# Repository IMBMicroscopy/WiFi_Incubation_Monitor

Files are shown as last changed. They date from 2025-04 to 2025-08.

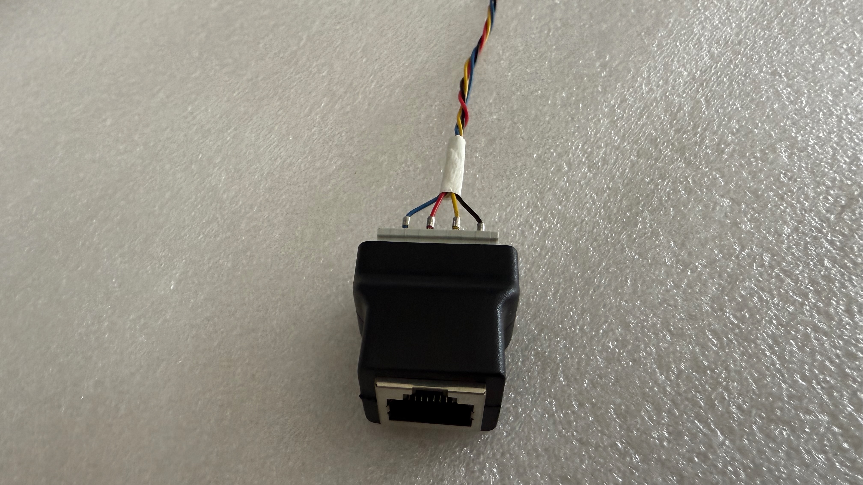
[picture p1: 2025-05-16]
Assembly Images/Front Side RJ45.jpeg

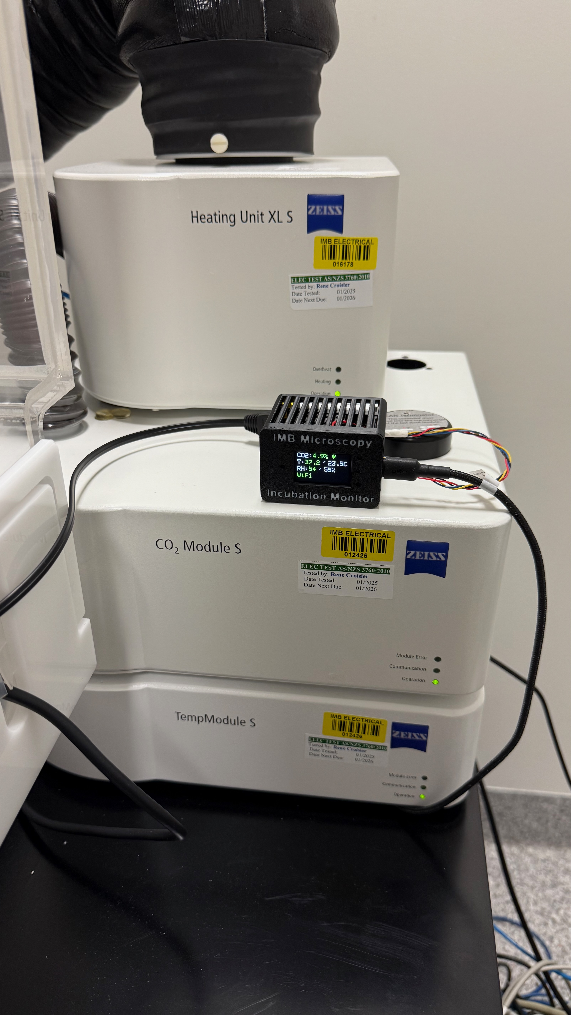
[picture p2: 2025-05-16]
Assembly Images/Monitoring CO2.jpeg

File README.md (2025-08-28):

# WiFi enabled Incubation Monitor

Author: Dr James Springfield (j.springfield@imb.uq.edu.au). 

Affiliation: Institute for Molecular Bioscience (IMB) Microscopy Facility, The University of Queensland. 

Date: June 2025. 

Real-Time Imaging Environment Monitoring Using an ESP32

We present a low-cost, open-source ESP32-based system for monitoring environmental conditions within live-cell imaging incubators. Each device integrates a 0–100% CO₂ sensor (with optional high-accuracy 0–1% sensor), along with temperature and humidity sensors. Optional features include pressure calibration and room environment monitoring.

A built-in TFT display and Adafruit IO dashboard provide real-time and remote data access. Sensor calibration compensates for temperature, humidity, and pressure. The system is user-friendly, requiring no soldering and offering hotspot-based configuration. It supports automated logging, WiFi setup, and dashboard customisation for scalable deployment across multiple incubators.

We are currently developing additional features, including Google Sheets integration for data logging, aligning with existing systems that track hardware and software usage during user sessions. These metrics are imported into Microsoft Power BI to generate dashboards that inform user needs and forecast future facility requirements.

updated incubation monitor





Pecon incubator lid inverted

Pecon lid installed

Monitoring CO2

## Monitor environmental conditions for live samples using an ESP32 device with STC31 CO2 sensor and SHTC3 temperature and relative humidity sensors

- Calibrate the CO2 sensor using Temperature, Humidity and Pressure
- Monitor LiPo battery SOC and discharge rate
- Report values to the TFT display, serial port and online dashboard
- **Each device will record the conditions for ONE incubator**
- **A free Adafruit IO account is required for logging of incubation conditions over time to the online dashboard**
  - https://accounts.adafruit.com/users/sign_in
  - You will then need the Username and Active Key values to load into the ESP32 device to enable data streaming.
  - **This must be done before configuring the hardware below**

**Required hardware:**

- Arduino compatible hardware such as: the following tested hardware
- Adafruit Feather ESP32-S3 reverse TFT mainboard such as https://learn.adafruit.com/esp32-s3-reverse-tft-feather (the code for the TFT has been optimised for this display size/resolution and will require modification for other displays)
- STC31 CO2 sensor board such as [https://www.sparkfun.com/products/18385](https://www.sparkfun.com/products/18385) or https://sensirion.com/products/catalog/SEK-STC31-C 
- Sparkfun Qwiic connector 500mm (or longer) cable: [https://www.sparkfun.com/products/17257](https://www.sparkfun.com/products/17257) (or you may manually solder the cables)
- This minimum configuration requires no soldering or electronics knowledge

**Required software libraries:**

- "SPI.h" built in library for SPI comms to tft display

- "WiFi.h" library for inbuit wifi comms to online dashboard

- "Preferences.h" for saving parameters to Flash for reuse later

- "SparkFun_STC3x_Arduino_Library.h" CO2 sensor library [http://librarymanager/All#SparkFun_STC3x](http://librarymanager/All#SparkFun_STC3x)

- "SparkFun_SHTC3.h" Temperature and Relative Humidity sensor library [http://librarymanager/All#SparkFun_SHTC3](http://librarymanager/All#SparkFun_SHTC3)

- "Adafruit_SHT4x.h" //SHT4x Temp/RH sensor library for use with the SEK-STC31-C development kit http://librarymanager/All#Adafruit SHT4x

- "Adafruit_GFX.h" Core graphics library for TFT display [http://librarymanager/All#Adafruit_GFX_Library](http://librarymanager/All#Adafruit_GFX_Library)

- "Adafruit_ST7789.h" Hardware-specific library for ST7789 controller [http://librarymanager/All#Adafruit_ST7789](http://librarymanager/All#Adafruit_ST7789)

- Adafruit IO Arduino Library [http://librarymanager/All#Adafruit_IO_Arduino](http://librarymanager/All#Adafruit_IO_Arduino)

  - "AdafruitIO_WiFi.h" for data feed functionality
  - "WiFiManager.h" for configuration of the sensors and WiFi

**Optional:**

- 3D printed case: AutoDesk Fusion https://a360.co/4j8FKbL or see included .3mf file
- Atmospheric pressure BME280 sensor [https://www.sparkfun.com/products/15440](https://www.sparkfun.com/products/15440) to measure atmospheric pressure for CO2 sensor calibration (also used for room T and RH monitoring)
- Adafruit BME280 Library for Environmental sensor [http://librarymanager/All#BME280](http://librarymanager/All#BME280)
- Low concentration CO2 sensor SCD41 [https://www.sparkfun.com/sparkfun-co-humidity-and-temperature-sensor-scd41-qwiic.html](https://www.sparkfun.com/sparkfun-co-humidity-and-temperature-sensor-scd41-qwiic.html)
- "SparkFun_SCD4x_Arduino_Library.h"  SCD41 CO2 sensor library [http://librarymanager/All#SparkFun_SCD4x](http://librarymanager/All#SparkFun_SCD4x)
- LiPo Battery for 3.7V - 4.2V such as 603450 with JST 2pin connector https://core-electronics.com.au/polymer-lithium-ion-battery-1000mah-38458.html
- "Adafruit_MAX1704X.h" library for lipo battery measurements [http://librarymanager/All#Adafruit_MAX1704X](http://librarymanager/All#Adafruit_MAX1704X)
- Additional short and long STEMMA/QWIIC connector I2C cables for the BME280 and SCD41 sensor boards as required (or just makeup and solder your own)

<br />
<br />

**Incubation Monitor Setup Instructions:**

**Configure Arduino IDE**

- Download and Install Arduino IDE: [https://www.arduino.cc/en/software](https://www.arduino.cc/en/software)
- Follow the instructions here: [https://learn.adafruit.com/esp32-s3-reverse-tft-feather/arduino-ide-setup-2](https://learn.adafruit.com/esp32-s3-reverse-tft-feather/arduino-ide-setup-2), to configure the Arduino IDE and to install the required drivers for the ESP32 board
- Using the library manager, search for and install required plugins for ESP32 and sensors as listed above
- Restart the Arduino IDE

**Configure and upload code**

- Within Arduino IDE, open the WiFi_Incubation_Monitor.ino file and wait for the associated files to load.
- Connect the sensors to the ESP32 using the I2C cable
- Connect the ESP32 to the computer via USB cable
- Go to "Tools" menu and select "Board" and select "ESP32", then select the "Adafruit Feather ESP-32 S3 Reverse TFT" board
- Go to "Tools" menu and select "Port" and then select the device that contains the "Adafruit Feather"
- Upload "Incubation_Monitor" sketch to ESP32 hardware (use the arrow button in the top left corner of the IDE), the device will restart when the upload is complete (if it doesnt, press the RST button on the ESP32)
- Click on the Arduino IDE serial monitor (top right corner of IDE) and ensure it is set to "Both NL & CR" and "115200 baud" to monitor the device setup progress
- The Mac address for the device will be displayed in the serial monitor, you may need to register this with your IT department to gain WiFi access to hidden WiFi networks
- For new hardware installs, the ESP32 will automatically create a hotspot as configured in the WiFi_Incubation_Monitor.ino file, default is "Incubation_Setup"

**Configure Hardware (ESP32)**
<br />

- On your PC/Phone/Tablet select the new temporary WiFi network "Incubation Setup", enter the password as per WiFi_Incubation_Monitor.ino and a popup window should appear after a few seconds

<br />
  
- **Dashboard users**
  - First, if you intend to use the Adafruit IO Dashboard, record your IO username and key, and decide on your dashboard name (name of incubator/microscope etc)
  - It's critical that you are within coverage range of your nearest WiFi access point in order to connect to the AP and then the IO Dashboard.
  - This is important, First, Click the "Setup" button to configure hardware parameters:
    - Enter the IO Dashboard values (**Username, Key and Dashboard name**)
    - Ensure "dashboard monitor" feature is toggled to "true"
    - Toggle the required installed sensors and their sensor parameters if they differ from the default settings in WiFi_Incubation_Monitor.ino file.
    - For further information about these parameters, consult the WiFi_Incubation_Monitor.ino file.
  - Click "Save", then click the "back arrow" button twice to go back to the home page.
  - Now, Click "Configure WiFi" to enter the SSID name and password, then click "Save".
  - The device will now attempt to connect to WiFi and if successful will close the popup window 
  - The device will then attempt to connect to the IO dashboard, before initialising the sensors and begin acquiring data.

<br />

- **Non Dashboard users**   
  - Click the "Setup" button to configure hardware parameters:
    - Ensure "dashboard monitor" feature is toggled to "false"
    - Toggle the required installed sensors and their sensor parameters if they differ from the default settings in WiFi_Incubation_Monitor.ino file.
    - For further information about these parameters, consult the WiFi_Incubation_Monitor.ino file.
  - Click "Save", then click the "back arrow" button twice to go back to the home page.
  - Now, Click "Exit" and the hotspot will close after about 10 seconds, the device will now initialise the sensors and begin acquiring data
  
<br />

**Adjust Parameters**

- To view the main parameters at any time, press the info page button (default=D1 pin)
- To adjust the Wifi and/or Adafruit parameters after initial setup and at any time, press the Reset button on the ESP32 device,
- Then when "Config -&gt;" appears on the display, press and hold the top right D0 button for one second,
- The "Incubation Setup" Wifi access point will appear on your network after a few seconds.
- Enter the hotspot password configured in the WiFi_Incubation_Monitor.ino file
- Then adjust the parameters in the "setup" and "Wifi setup" pages as required, then click Save
- To edit only the custom parameters on the setup page, you will first modify the parameters, click save, then go back to the homepage and click exit.

**Configure Adafruit IO Dashboard**

- If you havent already, you will need to create an account: https://accounts.adafruit.com/users/sign_in
- You will then need the Username and Active Key values to load into the ESP32 device to enable data streaming.
- Each incubation monitor will generally require a uniquely named dashboard to display its data feeds, these feeds are configured on the device after following the Incubation Monitor Setup Instructions steps above.
- You will need to create a unique data feed name prefix for each ESP32 based Incubation Monitor device, the device will then automatically create data feeds for each parameter: CO2, Temperature and Relative Humidity
- Once the ESP32 device is running and has started transmitting the data feeds, they should appear in the Data Feeds section of Adafruit IO
- Then you will need to create an Adafruit IO dashboard for each incubator with a graph to log the CO2, Temperature and Humidity values from the data feeds
- The CO2, Temperature and RH values must be assigned to a unique data feed name in the Adafruit IO dashboard
- ie: the Dashboard for the incubator would be the name of the microscope, ie: "Live Imager 1" and the data feed name prefix will be something like LI1 and will automatically create "LI1_probe_CO2", "LI1_probe_Temp" and "LI1_probe_RH"
- These will be the CO2, Temp and RH data feeds for the STC31 sensor on the long cable which is placed in the imaging chamber
- You can also enable "room_monitoring" in the configuration hotspot settings to create additional feeds from the optional bme280 sensor mounted in the 3D printed case, ie: "LI1_room_Temp", "LI1_room_RH" and "LI1_room_press"
- This can be used to monitor the environmental conditions in the microscope room, where the display unit is mounted, rather than in the imaging chamber
- Once the Dashboard is created, Create a new block such as a line graph and link them to the relevant datafeeds to display your data
- Edit the layout, to resize and position the blocks, then save your layout
- Adafruit IO allows you to publish read only versions of your dashboards to other websites for monitoring incubation conditions as well as configuring actions to send alert emails when conditions exceed limits



**Issues/Notes**

- Installation has been tested on Mac OS 15.3.1 with Arduino IDE 2.3.4
- The Arduino IDE Serial monitor can be used to monitor and debug operation of the unit if required (ensure "Both NL & CR" and the correct baud rate (115200 default))
- The BME280 may cause an I2C address conflict by default and you will need to change the address, either by setting the dipswitch to ON or installing a surface mount resistor to the address pad as per the board manufacturers instructions
- If you use a board other than the ESP32 reverse TFT, you may need to change the configuration hotspot trigger button assignment by altering "#define hotspotPin 2  // Pushbutton pin to activate hotspot for WiFi configuration" in initilise.ino 
  


- Due to the limited size of the included TFT display, some creativity was required to squish everything onto the display.
  - If "room_monitoring is enabled, additional Temperature and Relative Humidity values will be displayed in white after the probe values
  - "*" indicates the system is calibrating the CO2 sensor (rate is set in the code or via the configuration hotspot)
  - "WIFI" in green text indicates connected wifi, Yellow text indicates the wifi is asleep to save power, Red text indicates the WiFi connection has failed.
  - "^" indicates the system is uploading data to the dashboard (rate is set in the code or via the configuration hotspot)
  - the current CO2 reading reported on the TFT is selected by the "switchCO2Sensors" value, below which the lowCO2 sensor is used if active.
  - the battery discharge rate information doesnt currently fit on the display due to WiFi and IO indicators, so has been commented out in the code
- Additional sensors such as the BME280 (Environmental Sensor including Pressure) and SCD41 (low CO2) can be daisy chained in any order with the STC31 (high CO2 sensor) to the ESP32 using addtional I2C cables using the STEMMA/QWIIC connector or via solder joints  
- 3D Printed Case:
  -   The included 3D printed case file allows for a BME280 breakout board to be installed as well as a lithium ion battery inside the case (enable "Room Monitoring" in the configuration hotspot)
  -   However you may also mount the BME280 breakout board outside of the case in a location of your choosing such as the main incubation chamber of the microscope, to monitor ambient incubation conditions, and daisy chain on the SCD41 (low CO2) and STC31 breakout board (high CO2)   with another I2C cable to install inside the imaging chamber near the sample.
  -   In order to assemble the components within the 3d printed case, insert the ESP32 into the front case, gently spread the vertical panels and push down on the ESP32 until it seats under the latch,
  -   Install the cables onto the ESP32, then install the heatshields, then the bme280, route the battery and cabling, then install the battery support by pushing down until it clicks lightly.
  -   Place the battery on top of the support, pass the long sensor cable out through the hole in the back case, then install the case by sliding it over all of the components and pushing down until it clicks.
- Sensor Calibration:
  - The configuration hotspot contains settings for each sensor to offset the Temperature or CO2 values as well as perform a 2 point calbration for the Relative Humidity
  - Once built and configured you should ideally run the sensors for atleast 30mins to warm up and then place them in a known condition such as T, RH or CO2 and measure the offset and correct using the parameters available in the configuration hotspot
  - RH can be calibrated by using two known conditions of high and low RH at a measured temperature and applying these settings for each sensor

- Library versions tested
  - "SparkFun_STC3x_Arduino_Library.h" 1.0.0
  - "SparkFun_SHTC3.h" 1.1.4
  - "Adafruit_SHT4x.h" 1.0.5
  - "Adafruit_GFX.h" 1.12.0
  - "Adafruit_ST7789.h" 1.11.0
  - "Adafruit IO Arduino Library" 4.3.0
  - "WiFiManager" 2.0.17
  - "Adafruit BME280 Library" 2.2.4
  - "SparkFun_SCD4x_Arduino_Library.h" 1.1.2
  - "Adafruit_MAX1704X.h" 1.0.3

**Acknowledgements and License**

The author wishes to acknowledge the contributions from all of the hardware and software library creators that are featured in this code, without whom this tool would not be possible.  
Please see individual license files of each library for terms and conditions specific to that library.

MIT License
Copyright (c) \[2025\] \[James Springfield, The University of Queensland\]

Permission is hereby granted, free of charge, to any person obtaining a copy
of this software and associated documentation files (the "Software"), to deal
in the Software without restriction, including without limitation the rights
to use, copy, modify, merge, publish, distribute, sublicense, and/or sell
copies of the Software, and to permit persons to whom the Software is
furnished to do so, subject to the following conditions:

The above copyright notice and this permission notice shall be included in all
copies or substantial portions of the Software.

THE SOFTWARE IS PROVIDED "AS IS", WITHOUT WARRANTY OF ANY KIND, EXPRESS OR
IMPLIED, INCLUDING BUT NOT LIMITED TO THE WARRANTIES OF MERCHANTABILITY,
FITNESS FOR A PARTICULAR PURPOSE AND NONINFRINGEMENT. IN NO EVENT SHALL THE
AUTHORS OR COPYRIGHT HOLDERS BE LIABLE FOR ANY CLAIM, DAMAGES OR OTHER
LIABILITY, WHETHER IN AN ACTION OF CONTRACT, TORT OR OTHERWISE, ARISING FROM,
OUT OF OR IN CONNECTION WITH THE SOFTWARE OR THE USE OR OTHER DEALINGS IN THE
SOFTWARE.

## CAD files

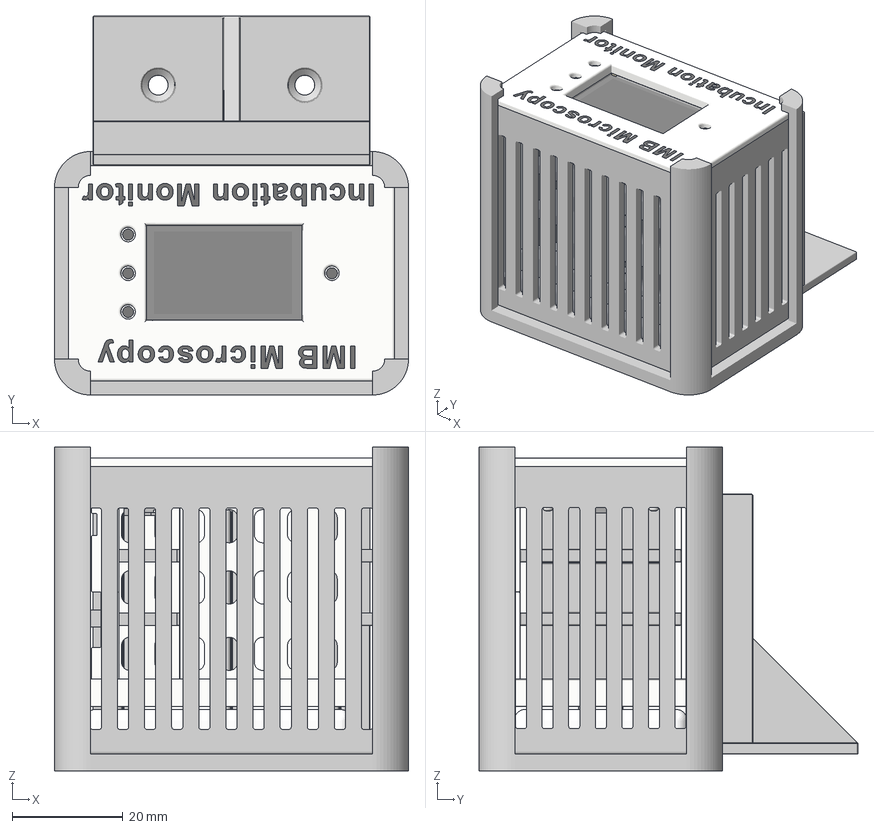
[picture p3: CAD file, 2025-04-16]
3D Printed Case/Incubation Monitor Case.3mf
64.0 x 68.5 x 58.5 mm
BME280
Back Case
Battery Support
Battery
Board
Front case
Heat Shield x 2
IMB Microscopy Text
Incubation Monitor Text
Mounting Bracket v2 x 2
Wall Bracket v1

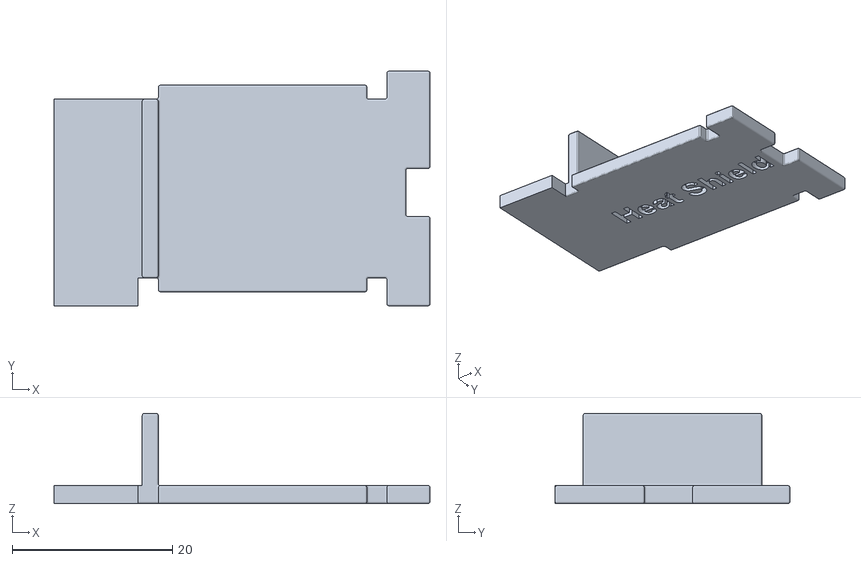
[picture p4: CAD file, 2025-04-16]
3D Printed Case/STLs/Heat Shield.stl
46.9 x 29.3 x 11.2

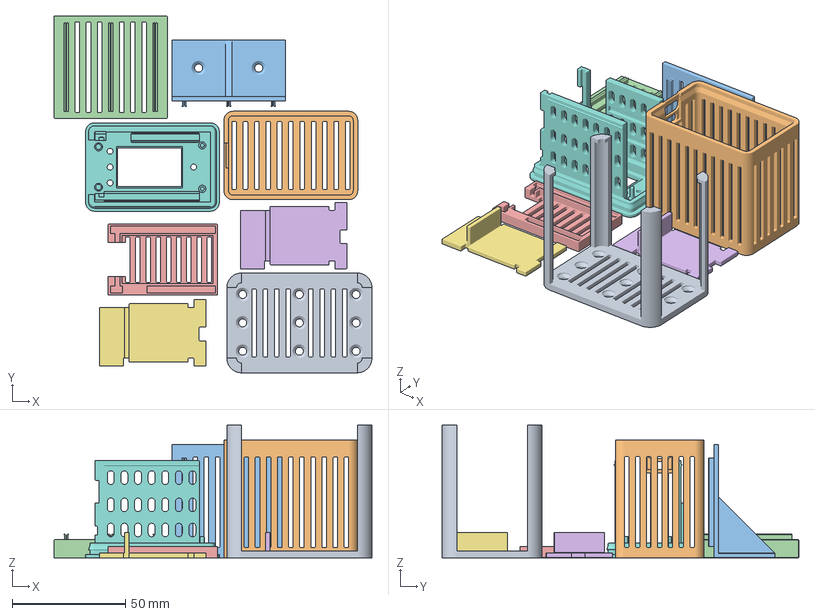
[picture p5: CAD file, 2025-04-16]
3D Printed Case/Incubation Monitor Case - Bambulab.3mf
140.2 x 157.2 x 58.5 mm
Wall Bracket v1
Back Case
Wall Bracket v2
Tripod Bracket
Battery Support
Heat Shield x 2
Front Case

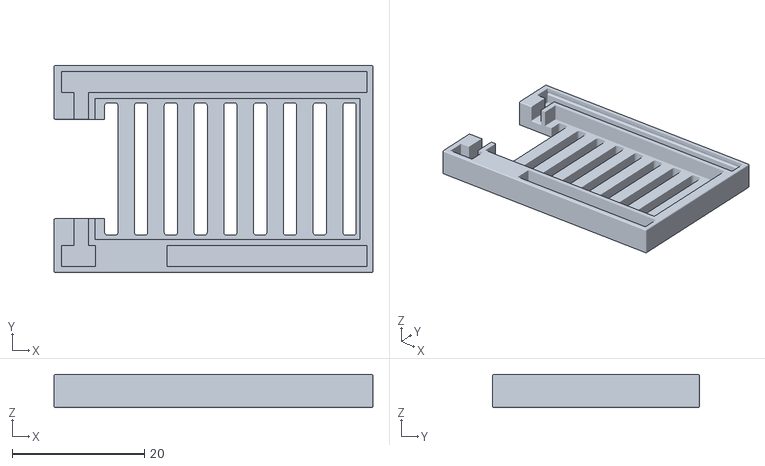
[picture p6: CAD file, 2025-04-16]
3D Printed Case/STLs/Battery Support.stl
48.2 x 31.3 x 5.00

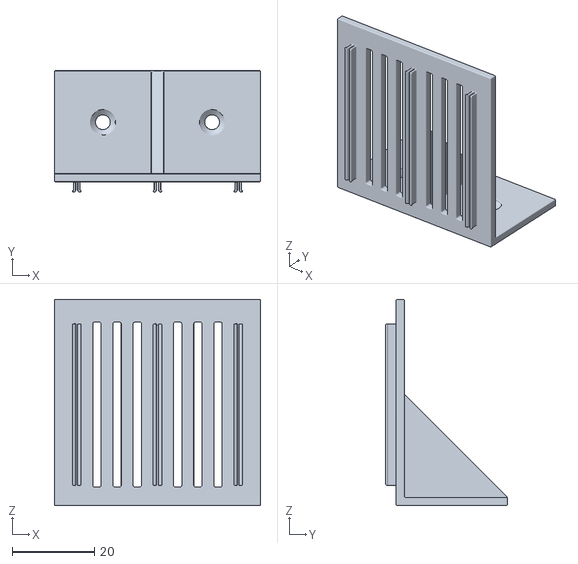
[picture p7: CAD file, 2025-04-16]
3D Printed Case/STLs/Wall Bracket v2.stl
50.0 x 29.5 x 50.0

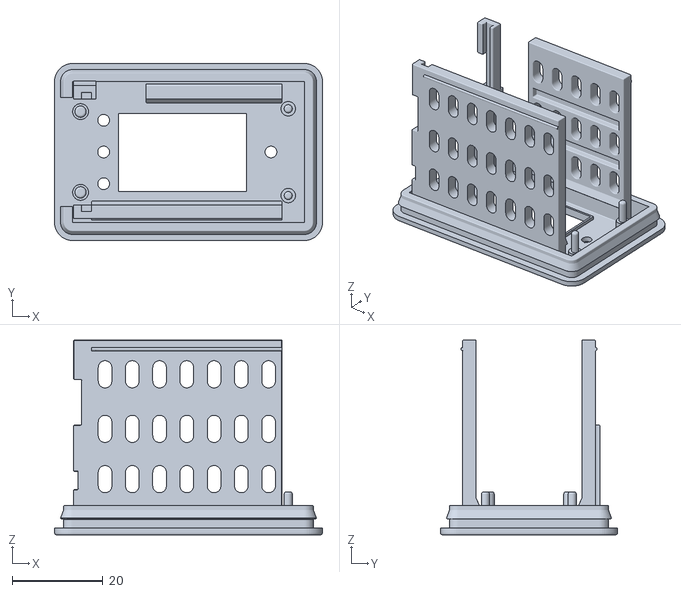
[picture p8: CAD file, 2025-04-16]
3D Printed Case/STLs/Front Case.stl
59.0 x 39.0 x 42.9

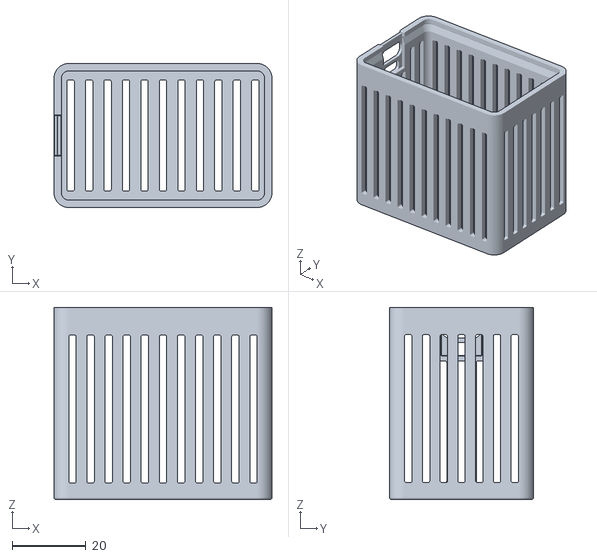
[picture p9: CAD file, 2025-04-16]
3D Printed Case/STLs/Back Case.stl
59.0 x 39.0 x 52.0

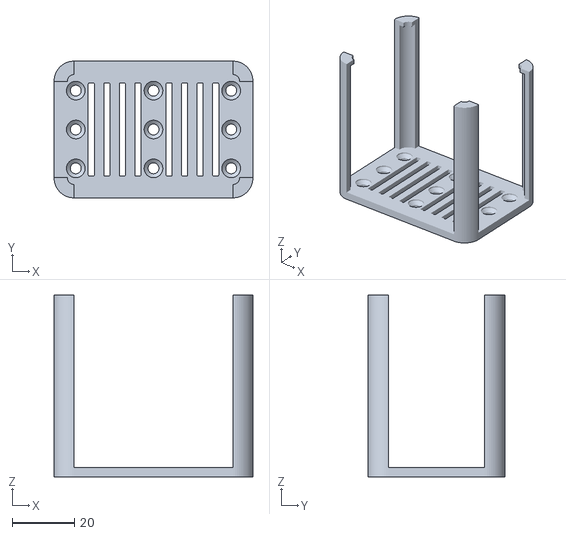
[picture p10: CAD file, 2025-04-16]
3D Printed Case/STLs/Wall Bracket v1.stl
64.0 x 44.0 x 58.5

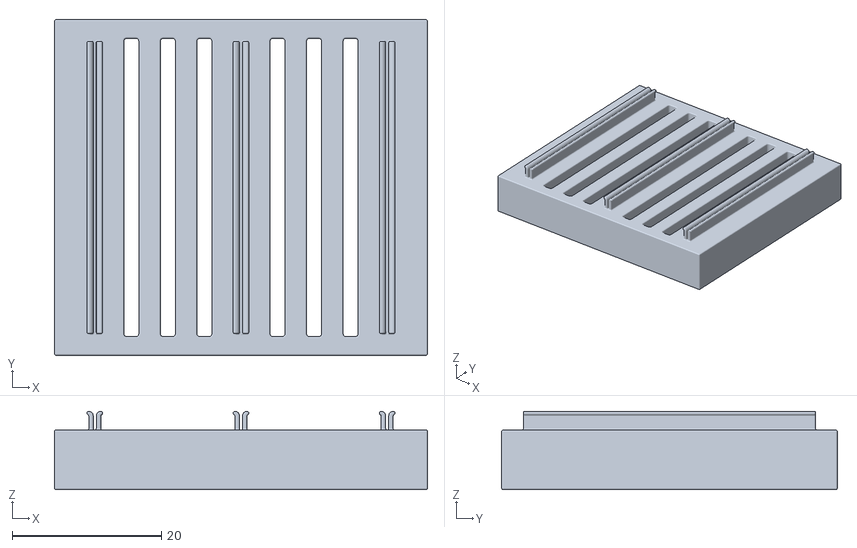
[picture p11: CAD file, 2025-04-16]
3D Printed Case/STLs/Tripod Bracket.stl
50.0 x 45.0 x 10.5

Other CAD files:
3D Printed Case/STLs/Heat Shield(1).stl

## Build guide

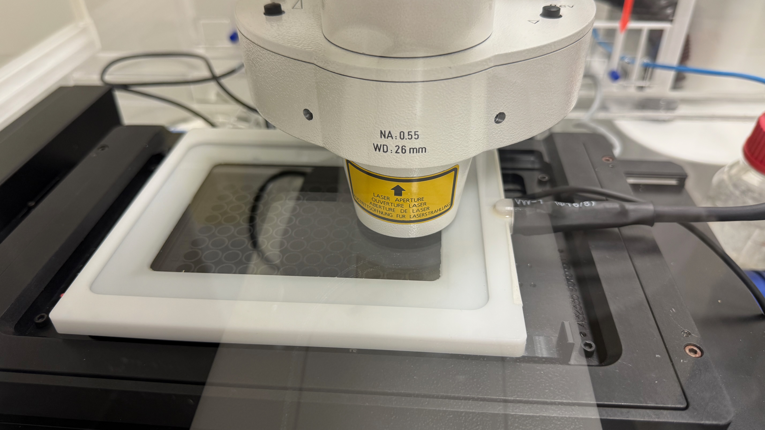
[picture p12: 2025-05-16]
Assembly Images/Pecon lid installed.jpeg

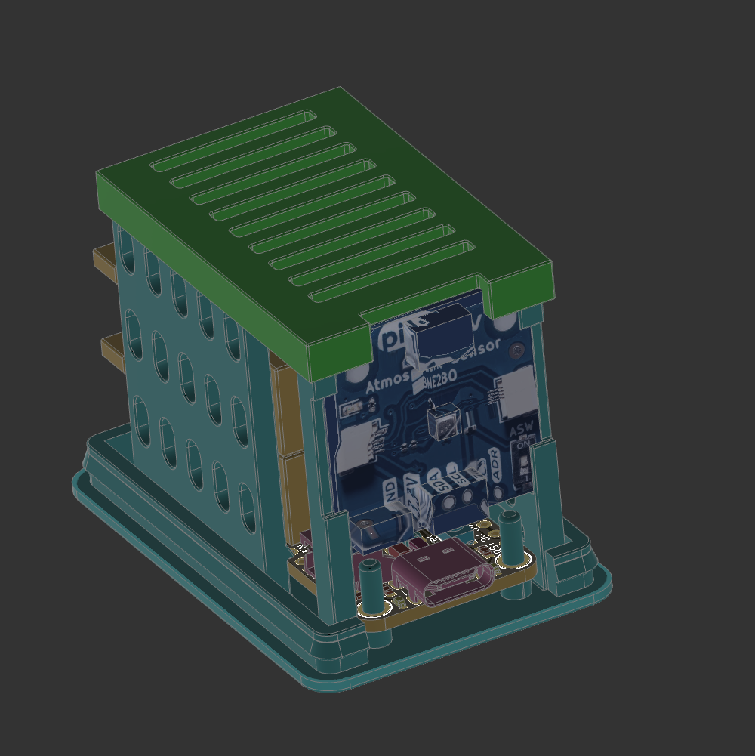
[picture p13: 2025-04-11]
Assembly Images/6 Battery Support.png

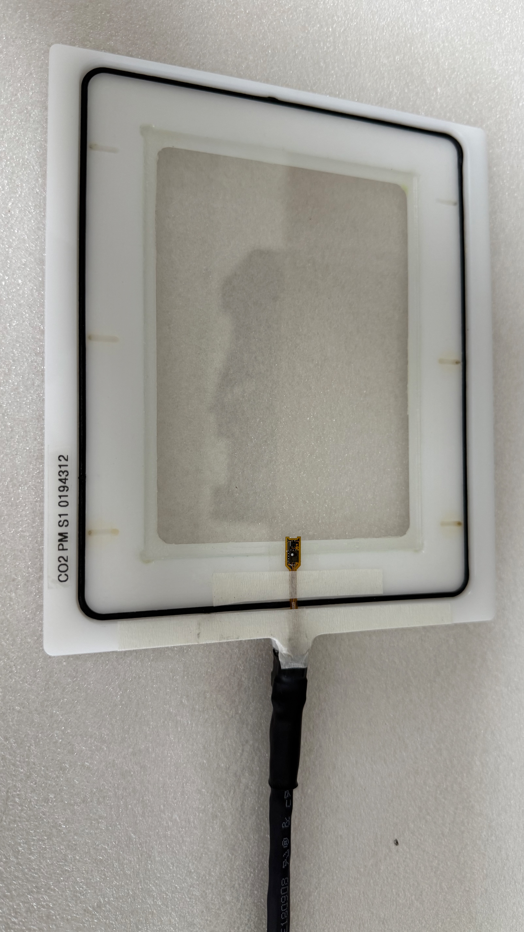
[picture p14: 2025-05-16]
Assembly Images/Pecon incubator lid inverted.jpeg

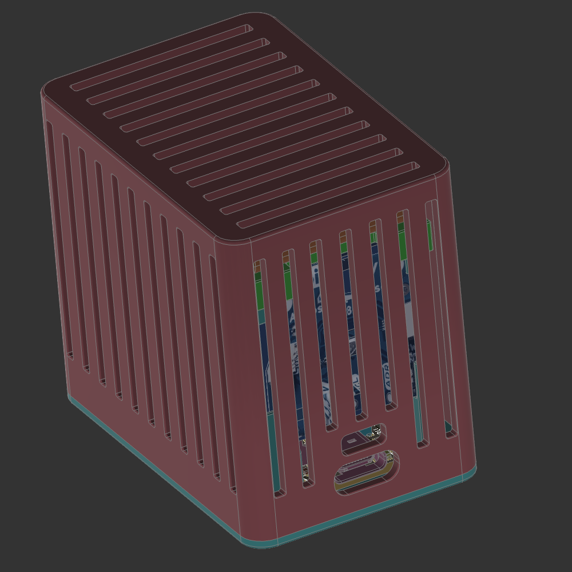
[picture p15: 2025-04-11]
Assembly Images/8 Back Case.png

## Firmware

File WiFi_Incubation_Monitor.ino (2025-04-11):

/*********************************************************************
 * User-Definable default Settings for the Incubation Monitor
 * These settings are the default settings installed onto the ESP32 device at first compile
 * and used on first load of the configuration hotspot, but may be altered and saved to flash from the hotspot
 * Adjust parameters as required
 *********************************************************************/

// -------------------------------------------------------------------
// Feature Toggles
// Set to false if you haven't installed the hardware or don't require the feature.
// -------------------------------------------------------------------
bool low_CO2_Monitor    = false; // Optional SCD41 sensor for measuring low ambient levels of CO2 (<1%)
bool high_CO2_Monitor   = true; // STC31 sensor (0.7 - 100% CO2) attached?
bool pressure_Monitor   = true; // Optional BME280 sensor for measuring ambient pressure and room conditions (T and RH)
bool battery_Monitor    = true; // Monitor battery charge if a battery is connected
bool dashboard_Monitor  = true; // Enable/disable online dashboard reporting (requires WiFi or Ethernet)
bool room_Monitor       = true; // if pressure_Monitor is true, Enable/disable reporting of T, RH and Pressure values from bme280 installed in the display case
//bool sleep_WiFi         = false; // Disable WiFi between dashboard updates to save battery power (feature not currently working reliably, disabled in initialise.ino and main.ino)
// -------------------------------------------------------------------
// CO2 Sensor Configuration
// -------------------------------------------------------------------
float switchCO2Sensors = 0.7; // Changeover from low-CO2 (SCD41) to high-CO2 (STC31) sensor. 
// If STC31 reading > 0.7%, use STC31; otherwise, use SCD41.
// the STC31 doesnt record below ~. 0.7% CO2
// ignored if low_CO2_Monitor = false

// -------------------------------------------------------------------
// Measurement Limits (Incubation Settings)
// Below or above these thresholds, an alarm condition (e.g., TFT color change) occurs
// -------------------------------------------------------------------
float lowCO2   = 4.0;   // CO2 % value BELOW this triggers an alarm
float highCO2  = 6.0;   // CO2 % value ABOVE this triggers an alarm
float lowRH    = 40;  // Relative humidity % BELOW this triggers an alarm
float highRH   = 100; // Relative humidity % ABOVE this triggers an alarm
float lowTemp  = 35;  // Temperature (°C) BELOW this triggers an alarm
float highTemp = 38;  // Temperature (°C) ABOVE this triggers an alarm
float pressure  = 1020.0;  // Ambient average pressure (mbar) used for CO2 calibration if no BME280 pressure sensor is installed

// -------------------------------------------------------------------
// Battery Settings
// -------------------------------------------------------------------
float lowBatt = 20; // Battery State of Charge (SOC) in % BELOW this triggers an alarm (changes colour on the display)

// -------------------------------------------------------------------
// Measurement Rates (in seconds) (values will be constrained automatically in code as per requirements below)
// -------------------------------------------------------------------
int sensorRate      = 15;  // Read sensors and update TFT every X seconds (>=1)
int compensateRate  = 15;  // Recalibrate CO2 sensor (T, RH, Pressure) every X seconds (>= sensorRate)
int dashboardRate   = 60;  // Update the online dashboard every X seconds (>= sensorRate)
int batteryRate     = 300; // Check BMS hibernation status and wake if needed (>= sensorRate)

// -------------------------------------------------------------------
// bme280 calibration (in case for room monitoring)
// -------------------------------------------------------------------
float bme280_offsetTemp = 0;  //offset bme280 temperature to match other sensors

bool bme280_calibrateRH = false;  //Optionally: Use a humidity controlled environment to calibrate the bme280 Humidity Sensor
//Calibration standards such as salt media (NaCL and MgCL) or an electronically controlled humidity chamber can be used
//Place saturated salt solution (salt + a little water) in an airtight container.
//75% RH (NaCl) and 33% RH (MgCl₂)
//Place sensor in chamber, wait 24hrs or until value plateaus before recording measurement
float bme280_high_reference = 76;   // High reference humidity chamber value (70-100%) or validated sensor reading 
float bme280_high_reading = 64;     // BME280 measured value when sensor is measuring in high_reference value chamber
float bme280_low_reference = 14;    // Low reference humidity chamber value (10-30%) or validated sensor reading
float bme280_low_reading = 10;      // BME280 measured value when sensor is measuring in low_reference value chamber

// -------------------------------------------------------------------
// STC31 calibration 
// -------------------------------------------------------------------
float stc31_offsetCO2 = 0;  //offset STC31 CO2 value to match calibration standard

// -------------------------------------------------------------------
// SHT calibration (on High CO2 STC31 sensor board)
// -------------------------------------------------------------------
float sht_offsetTemp = 0;  // Offset SHTC3 temperature to match other sensors

bool sht_calibrateRH = false;  // Optionally: Use a humidity-controlled environment to calibrate the SHTC3 Humidity Sensor
// Calibration standards such as salt media (NaCl and MgCl₂) or an electronically controlled humidity chamber can be used
// Place saturated salt solution (salt + a little water) in an airtight container.
// 75% RH (NaCl) and 33% RH (MgCl₂)
// Place sensor in chamber, wait 24hrs or until value plateaus before recording measurement
float sht_high_reference = 75;    // High reference humidity chamber value (70-100%) or validated sensor reading
float sht_high_reading = 75;      // SHTC3 measured value when sensor is measuring in high_reference value chamber
float sht_low_reference = 33;     // Low reference humidity chamber value (10-30%) or validated sensor reading
float sht_low_reading = 33;       // SHTC3 measured value when sensor is measuring in low_reference value chamber

// -------------------------------------------------------------------
// SCD41 calibration (on Low CO2 sensor board)
// -------------------------------------------------------------------
float SCD41_offsetTemp = 0;  // Offset SCD41 temperature to match other sensors

bool SCD41_calibrateRH = false;  // Optionally: Use a humidity-controlled environment to calibrate the SCD41 Humidity Sensor
// Calibration standards such as salt media (NaCl and MgCl₂) or an electronically controlled humidity chamber can be used
// Place saturated salt solution (salt + a little water) in an airtight container.
// 75% RH (NaCl) and 33% RH (MgCl₂)
// Place sensor in chamber, wait 24hrs or until value plateaus before recording measurement
float SCD41_high_reference = 75;    // High reference humidity chamber value (70-100%) or validated sensor reading
float SCD41_high_reading = 75;      // SCD41 measured value when sensor is measuring in high_reference value chamber
float SCD41_low_reference = 33;     // Low reference humidity chamber value (10-30%) or validated sensor reading
float SCD41_low_reading = 33;       // SCD41 measured value when sensor is measuring in low_reference value chamber

// -------------------------------------------------------------------
// Additional Parameters (values below are not configurable in hotspot)
// -------------------------------------------------------------------
int  baud = 115200;  // Serial port baud rate

char hotspotSSID[64] = "Incubation Setup";  // SSID for the configuration hotspot
char hotspotPWD[64]  = "setup123";         // Password (must be exactly 8 chars)
int  hotspotTimer    = 15;                 // Seconds to wait after reboot to allow a user to activate the config hotspot

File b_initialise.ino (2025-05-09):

#define SOFTWARE_VERSION "1.5.2"

// Define constants and parameters
#define infoPin 1 // Pushbutton pin to activate info screen
#define hotspotPin 2  // Pushbutton pin to activate hotspot for WiFi configuration


// Include required libraries
#include "esp_mac.h"             // Exposes esp_mac_type_t values
#include <cstring>               // For strcmp, strcpy, strcasecmp
#include <Wire.h>                // I2C communications for CO2 sensor breakout board
#include <SPI.h>                 // SPI interface for TFT display
#include <Adafruit_Sensor.h>     // Adafruit sensor library
#include <Adafruit_GFX.h>        // Core graphics library for TFT
#include <Adafruit_ST7789.h>     // Hardware-specific library for ST7789

Adafruit_ST7789 tft = Adafruit_ST7789(TFT_CS, TFT_DC, TFT_RST); // TFT variable for Adafruit Feather

// Include sensor libraries
#include "Adafruit_MAX1704X.h"   // LiPo battery measurements
Adafruit_MAX17048 maxlipo;       // Battery monitor variable

#include <Adafruit_BME280.h>
Adafruit_BME280 myBME280;

#include "SparkFun_SCD4x_Arduino_Library.h"  // SCD41 CO2 sensor library
SCD4x mySCD41;

#include "SparkFun_STC3x_Arduino_Library.h"  // STC31 high CO2 % sensor library
STC3x mySTC31;

#include "Adafruit_SHT4x.h" //SHT4x Temp/RH sensor library
Adafruit_SHT4x mySHT4 = Adafruit_SHT4x();

#include "SparkFun_SHTC3.h"  // SHTC3 Temp/RH sensor library
SHTC3 mySHTC3;


// WiFi and IO libraries
#include <WiFiManager.h>
#include <WiFi.h>
#include "AdafruitIO_WiFi.h"

// save parameters to preferences file
#include <Preferences.h>
Preferences preferences;

// WiFi Manager parameters stored in character array buffers
char IO_USERNAME_buff[64] = "";
char IO_KEY_buff[64] = "";
char IO_Dashboard_buff[64] = "";
char CO2_FeedName_buff[64] = "";
char Temp_FeedName_buff[64] = "";
char RH_FeedName_buff[64] = "";
char roomTemp_FeedName_buff[64] = "";
char roomRH_FeedName_buff[64] = "";
char roomPress_FeedName_buff[64] = "";

//optional configuration parameters to store character array of values for use in WiFiManager
//Feature Toggles
char low_CO2_Monitor_buff[6] = "";
char high_CO2_Monitor_buff[6] = "";
char pressure_Monitor_buff[6] = "";
char battery_Monitor_buff[6] = "";
char dashboard_Monitor_buff[6] = "";
char room_Monitor_buff[6] = "";
char sleep_WiFi_buff[6] = "";
//Sensor Settings
char switchCO2Sensors_buff[8] = "";
char lowCO2_buff[8] = "";
char highCO2_buff[8] = "";
char lowRH_buff[8] = "";
char highRH_buff[8] = "";
char lowTemp_buff[8] = "";
char highTemp_buff[8] = "";
char lowBatt_buff[8] = "";
char pressure_buff[8] = "";
//Update rates
char sensorRate_buff[8] = "";
char compensateRate_buff[8] = "";
char dashboardRate_buff[8] = "";
char batteryRate_buff[8] = "";
// STC31 calibration
char stc31_offsetCO2_buff[8] = "";
// BME280 calibration
char bme280_offsetTemp_buff[8] = "";
char bme280_calibrateRH_buff[6] = "";
char bme280_high_reference_buff[8] = "";
char bme280_high_reading_buff[8] = "";
char bme280_low_reference_buff[8] = "";
char bme280_low_reading_buff[8] = "";
// SHT calibration
char sht_offsetTemp_buff[8] = "";
char sht_calibrateRH_buff[6] = "";
char sht_high_reference_buff[8] = "";
char sht_high_reading_buff[8] = "";
char sht_low_reference_buff[8] = "";
char sht_low_reading_buff[8] = "";
// SCD41 calibration
char SCD41_offsetTemp_buff[8] = "";
char SCD41_calibrateRH_buff[6] = "";
char SCD41_high_reference_buff[8] = "";
char SCD41_high_reading_buff[8] = "";
char SCD41_low_reference_buff[8] = "";
char SCD41_low_reading_buff[8] = "";
//Additional
//char baud_buff[8] = "";

// Adafruit IO variables
static uint8_t objStorage[sizeof(AdafruitIO_WiFi)];
AdafruitIO_WiFi *io;        // Adafruit IO pointer
AdafruitIO_Feed *CO2_Feed;  //CO2 data feed to IO dashboard
AdafruitIO_Feed *Temp_Feed; //Temp data feed to IO dashboard
AdafruitIO_Feed *RH_Feed;   //RH data feed to IO dashboard
AdafruitIO_Feed *roomTemp_Feed;   //room Temperature data feed to IO dashboard
AdafruitIO_Feed *roomRH_Feed;   //room RH data feed to IO dashboard
AdafruitIO_Feed *roomPress_Feed;   //room Pressure data feed to IO dashboard

// Create WiFiManager object and custom parameters to display on hotspot website
WiFiManager wifiManager;
WiFiManagerParameter custom_dashboard_title("<p>-------------------IO Dashboard Parameters-------------------</p>");
WiFiManagerParameter custom_IO_USERNAME("io_user", "Adafruit IO Username", IO_USERNAME_buff, 60);
WiFiManagerParameter custom_IO_KEY("io_key", "Adafruit IO Key", IO_KEY_buff, 60);
WiFiManagerParameter custom_IO_Dashboard("io_dashboard", "Adafruit IO Data Feed Prefix", IO_Dashboard_buff, 60);
// Optional WiFiManager parameters
WiFiManagerParameter custom_monitor_title("<p>-------------------Feature Toggles-------------------</p>");
WiFiManagerParameter custom_low_CO2_Monitor("low_CO2_Monitor", "low CO2 monitor - monitor 0-1% CO2 (true/false)", low_CO2_Monitor_buff, 6);
WiFiManagerParameter custom_high_CO2_Monitor("high_CO2_Monitor", "high CO2 monitor - monitor 1-100% CO2 (true/false)", high_CO2_Monitor_buff, 6);
WiFiManagerParameter custom_pressure_Monitor("pressure_Monitor", "pressure monitor - use bme280 sensor (true/false)", pressure_Monitor_buff, 6);
WiFiManagerParameter custom_battery_Monitor("battery_Monitor", "battery monitor - report BMS values (true/false)", battery_Monitor_buff, 6);
WiFiManagerParameter custom_dashboard_Monitor("dashboard_Monitor", "dashboard monitor - update online dashboard (true/false)", dashboard_Monitor_buff, 6);
WiFiManagerParameter custom_room_Monitor("room_Monitor", "Room monitor (true/false)", room_Monitor_buff, 6);
WiFiManagerParameter custom_sleep_WiFi("sleep_WiFi", "Sleep WiFi - to save battery power (true/false)", sleep_WiFi_buff, 6);
//Sensor parameters
WiFiManagerParameter custom_sensor_title("<p>----------------------Sensor Parameters----------------------</p>");
WiFiManagerParameter custom_switch_CO2_Sensors("switch_CO2_Sensors", "switch between CO2 sensors (%)", switchCO2Sensors_buff, 8);
WiFiManagerParameter custom_lowCO2("low_CO2", "low CO2 alert (%)", lowCO2_buff, 8);
WiFiManagerParameter custom_highCO2("high_CO2", "high CO2 alert (%)", highCO2_buff, 8);
WiFiManagerParameter custom_lowRH("low_RH", "low RH alert (%)", lowRH_buff, 8);
WiFiManagerParameter custom_highRH("high_RH", "high RH alert (%)", highRH_buff, 8);
WiFiManagerParameter custom_lowTemp("low_Temp", "low Temp alert (C)", lowTemp_buff, 8);
WiFiManagerParameter custom_highTemp("high_Temp", "high Temp alert (C)", highTemp_buff, 8);
WiFiManagerParameter custom_lowBatt("low_Batt", "low Battery alert (%)", lowBatt_buff, 8);
WiFiManagerParameter custom_pressure("pressure", "manual pressure value (mbar)", pressure_buff, 8);
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

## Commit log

2025-03-08 added 3d case file
    [Incubation Monitor Case v5.3mf]
2025-03-08 added 3d printed case
    [Incubation Monitor Case v5.3mf]
2025-03-08 added STLs
    [Back Case.stl, Battery Support.stl, Front face.stl, Heat Shield.stl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]
2025-03-08 updated 3d files
    [Back Case.stl, Incubation Monitor Case v5.3mf]
2025-03-08 updated case vents
    [Back Case.stl, Battery Support.stl, Front face.stl, Heat Shield.stl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]
2025-03-08 updated 3d case
    [Back Case.stl, Incubation Monitor Case v5.3mf]
2025-03-11 bme280 calibration
    added 2point calibration for bme280 humidity and offset temp
    added room monitor data feeds
2025-03-11 fixed upper case
    hotspot wasnt accepting upper case letters in bool values
2025-03-12 added calibration for all sensors
    also tweaked reading the sensors as i didnt realise they werent always returning a value
    [Back Case.stl, Battery Support.stl, Front face.stl, Heat Shield.stl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]
2025-03-13 disabled wifi when dashboard is disabled
    save power hopefully
2025-03-13 added low power wifi mode
    turn off wifi when not required
    need to still add it to the config hotspot as a toggle
2025-03-21 bug in saving params
    since i removed baud rate, the test failed to check if params existed in flash, so changed to using pressure key
2025-04-11 added STC31 CO2 offset and SHT4 library for SEK-STC31 sensor
2025-04-14 version 1.3.0
    added Pressure to tft when only performing room monitoring
2025-04-14 updated 3d printed case
    added wall bracket and provided more room for probe cable
    [Incubation Monitor Case side mount.3mf, Incubation Monitor Case.3mf]
2025-04-14 updated 3d case files
    [Incubation Monitor Case - Bambulab.3mf]
2025-04-16 v1.3.2 release
    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
2025-04-17 v1.4.2
    added info page to display parameters without restarting device
    default action is to trigger the D1 pin
2025-04-17 v1.5.0
    added automatic high CO2 sensor detection,
    so it doesnt have to be defined in the code
2025-04-17 removed test code
    was attempting to average CO2 values which fluctuate on the SEK-STC31-C device, but the readout time needs to be atleast 1s, and the benefit is minimal
2025-05-16 assembly images for SEK-STC31
